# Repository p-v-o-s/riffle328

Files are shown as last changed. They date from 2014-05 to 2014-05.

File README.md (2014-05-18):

riffle328
=========

"Riffle in a Bottle"

A lower-functionality / higher cost / Arduino IDE - compatible [Riffle](http://publiclab.org/wiki/riffle), based on Atmel328p.

- Requires FTDI cable for programming (e.g. Adafruit's "FTDI Friend") -- typically $15
- Includes uSD, flash memory, high-precision real time clock (DS3231) with coin battery backup
- Programmable as "Arduino UNO" in Arduino IDE
- runs at 3.3V and 16 MHz
- includes circuit for monitoring battery level
- board width allows device to be inserted through mouth of standard plastic water bottle (one with 20 mm diameter or greater)
- can run for several weeks (perhaps months) on 3 AA batteries, especially if low self-discharging batteries (like rechargeable Eneloops) are used
- Rough estimate of cost of parts that could be used to log temperature in a water bottle (not including shipping, or FTDI cable): $38 -- cost estimate [here](https://docs.google.com/spreadsheets/d/1v0O8HmP8-q_kPunHILv5Io3zThpqvPBZZoY3aYnxRDc/edit#gid=0)

### Usage

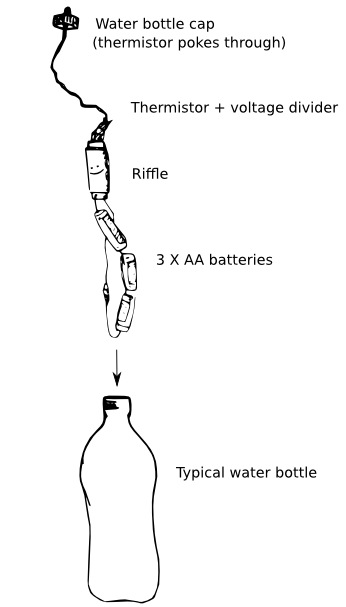
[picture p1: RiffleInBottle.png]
Optional title


- For a diagram of pin locations and optional configurations, please see this [diagram in PDF format](https://github.com/p-v-o-s/riffle328/blob/master/riffleUsage.pdf)

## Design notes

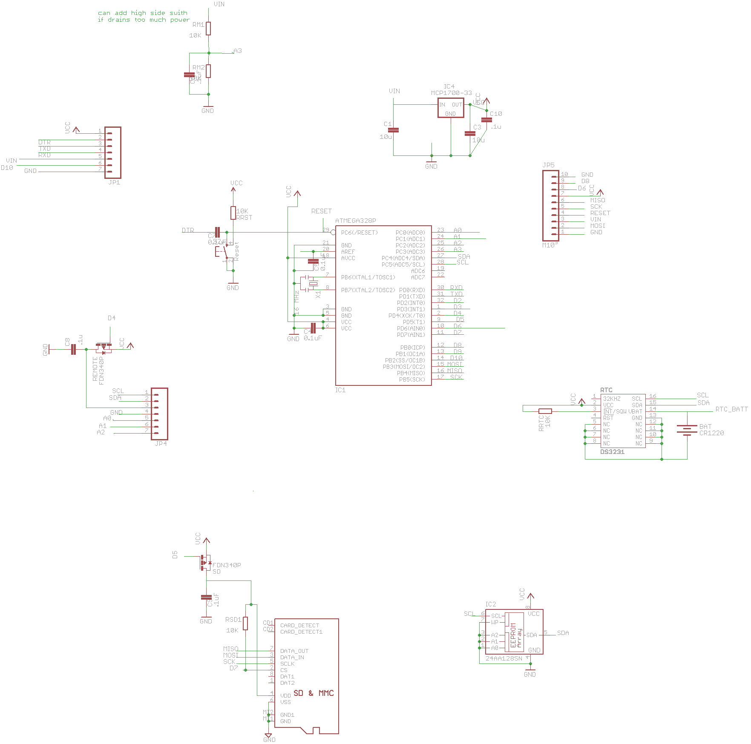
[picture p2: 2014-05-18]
REVA1/riffle328-REVA-schem.png

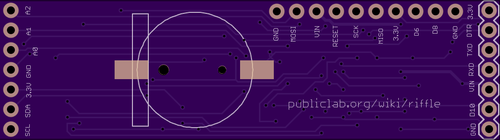
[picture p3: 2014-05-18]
REVA1/riffle328REVA-oshback.png

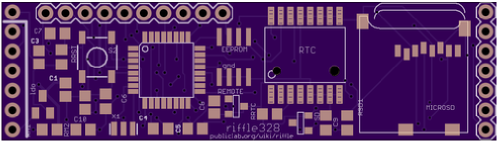
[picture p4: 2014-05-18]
REVA1/riffle328REVA-oshfront.png

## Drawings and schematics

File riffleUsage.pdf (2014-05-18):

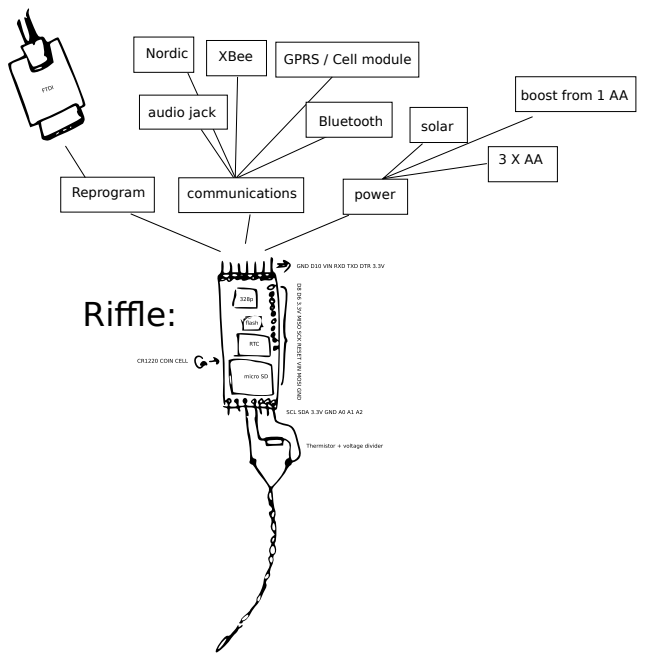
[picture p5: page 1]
Bluetooth; Riffle:; XBee; GPRS / Cell module; power; solar; Reprogram; Nordic; communications; audio jack

boost from 1 AA

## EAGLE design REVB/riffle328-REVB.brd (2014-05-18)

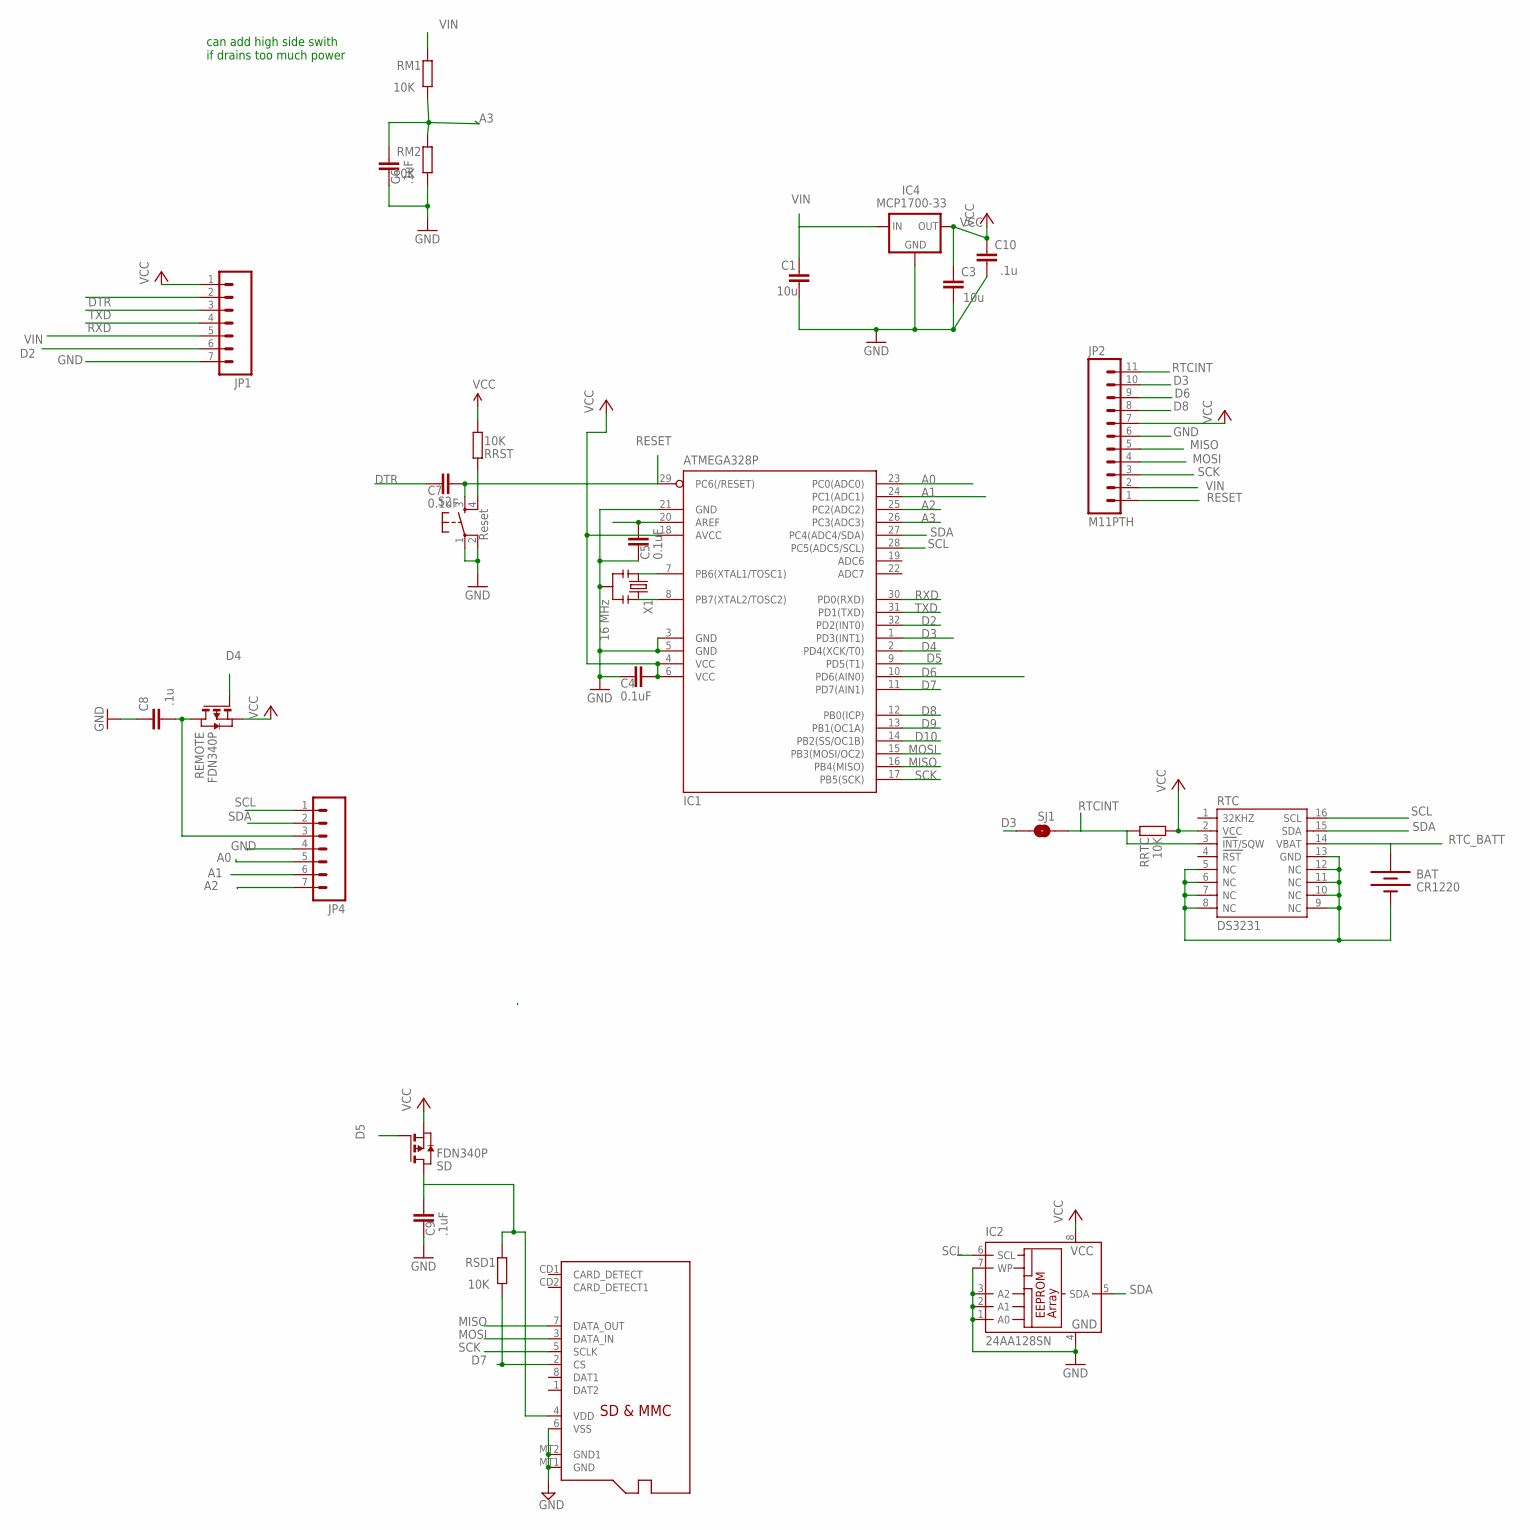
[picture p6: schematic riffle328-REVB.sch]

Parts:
BAT: CR1220; BATTCON_12MM_SMT
C1, C3: 10u; C0805
C4, C5, C7: 0.1uF; C0805@1
C6, C9: .1uF; C0805@1
C8, C10: .1u; C0805
IC1: ATMEGA328P; TQFP32-08
IC2: 24AA128SN; SO-08
IC4: MCP1700-33; SOT23
JP1, JP4: M07; 1X07
JP2: M11PTH; 1X11
MICROSD: MICROSD
REMOTE: FDN340P; SOT-23
RM1, RM2: 10K; R0805
RRST: 10K; R0805
RRTC: 10K; R0805
RSD1: 10K; R0805
RTC: DS3231
S2: Reset; TACTILE_SWITCH_SMD
SD: FDN340P; SOT-23
SJ1: SOLDERJUMPERNO; SJ_2S-NO
X1: 16 MHz; RESONATOR-SMD

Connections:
A0: IC1.23 (PC0(ADC0)), JP4.5
A1: IC1.24 (PC1(ADC1)), JP4.6
A2: IC1.25 (PC2(ADC2)), JP4.7
A3: C6.2, IC1.26 (PC3(ADC3)), RM1.1, RM2.2
AREF: C5.2, IC1.20 (AREF)
D2: IC1.32 (PD2(INT0)), JP1.6
D3: IC1.1 (PD3(INT1)), JP2.10, SJ1.2
D4: IC1.2 (PD4(XCK/T0)), REMOTE.3 (G)
D5: IC1.9 (PD5(T1)), SD.3 (G)
D6: IC1.10 (PD6(AIN0)), JP2.9
D7: IC1.11 (PD7(AIN1)), MICROSD.2 (CS), RSD1.1
D8: IC1.12 (PB0(ICP)), JP2.8
D9: IC1.13 (PB1(OC1A))
D10: IC1.14 (PB2(SS/OC1B))
DTR: C7.1, JP1.2
GND: BAT.P$1 (-), C1.2, C3.2, C4.1, C5.1, C6.1, C8.1, C9.1, C10.2, IC1.3 (GND), IC1.5 (GND), IC1.21 (GND), IC2.1 (A0), IC2.2 (A1), IC2.3 (A2), IC2.4 (GND), IC2.7 (WP), IC4.1 (GND), JP1.7, JP2.6, JP4.4, MICROSD.6 (VSS), MICROSD.MT1 (GND), MICROSD.MT2 (GND1), RM2.1, RTC.5 (NC), RTC.6 (NC), RTC.7 (NC), RTC.8 (NC), RTC.9 (NC), RTC.10 (NC), RTC.11 (NC), RTC.12 (NC), RTC.13 (GND), S2.1, S2.2, X1.2
MISO: IC1.16 (PB4(MISO)), JP2.5, MICROSD.7 (DATA_OUT)
MOSI: IC1.15 (PB3(MOSI/OC2)), JP2.4, MICROSD.3 (DATA_IN)
unnamed: IC1.8 (PB7(XTAL2/TOSC2)), X1.3
unnamed: IC1.7 (PB6(XTAL1/TOSC1)), X1.1
RESET: C7.2, IC1.29 (PC6(/RESET)), JP2.1, RRST.2, S2.3, S2.4
RTCINT: JP2.11, RRTC.2, RTC.3 (INT/SQW), SJ1.1
RTC_BATT: BAT.P$2 (+), RTC.14 (VBAT)
RXD: IC1.30 (PD0(RXD)), JP1.4
SCK: IC1.17 (PB5(SCK)), JP2.3, MICROSD.5 (SCLK)
SCL: IC1.28 (PC5(ADC5/SCL)), IC2.6 (SCL), JP4.1, RTC.16 (SCL)
SDA: IC1.27 (PC4(ADC4/SDA)), IC2.5 (SDA), JP4.2, RTC.15 (SDA)
TXD: IC1.31 (PD1(TXD)), JP1.3
VCC: C3.1, C4.2, C8.2, C10.1, IC1.4 (VCC), IC1.6 (VCC), IC1.18 (AVCC), IC2.8 (VCC), IC4.2 (OUT), JP1.1, JP2.7, JP4.3, REMOTE.1 (D), REMOTE.2 (S), RRST.1, RRTC.1, RTC.2 (VCC), SD.2 (S)
VDD: C9.2, MICROSD.4 (VDD), RSD1.2, SD.1 (D)
VIN: C1.1, IC4.3 (IN), JP1.5, JP2.2, RM1.2

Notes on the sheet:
can add high side swith if drains too much power

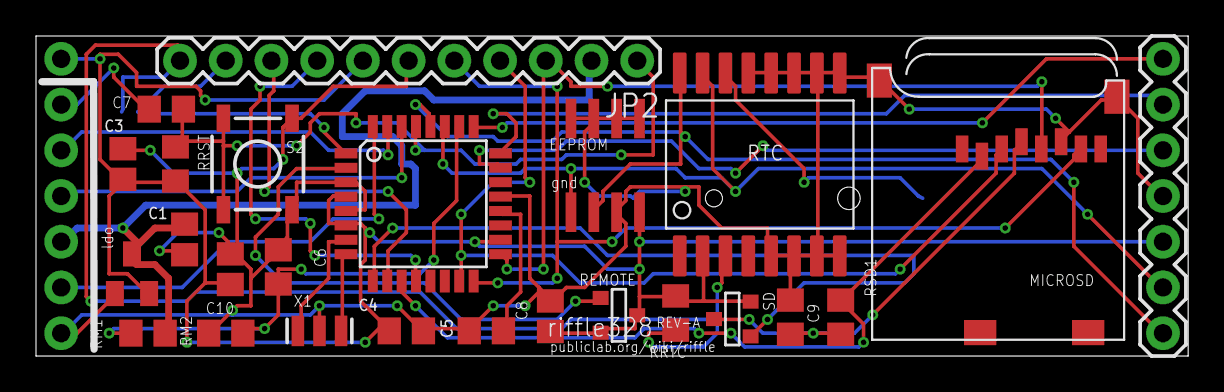
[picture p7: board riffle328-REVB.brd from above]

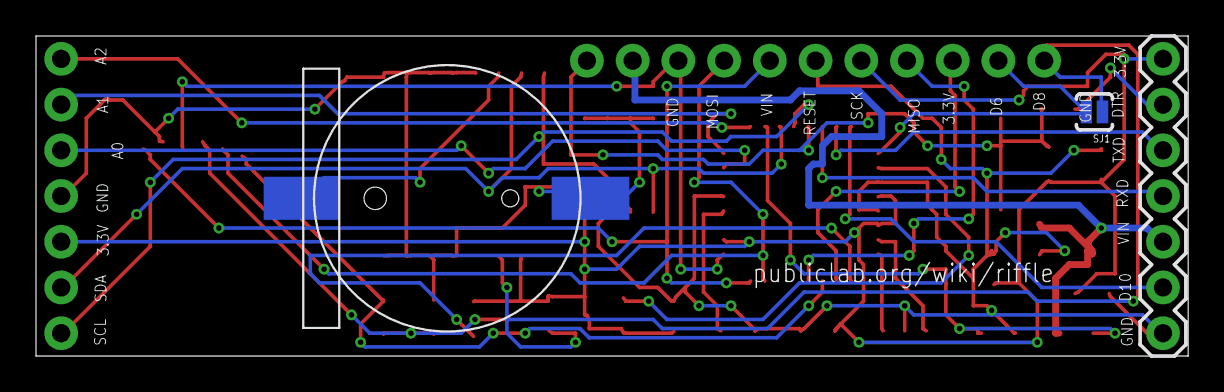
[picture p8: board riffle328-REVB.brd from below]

Board: 4 copper layers, 64.0 x 17.8 mm, 28 parts (3 on the bottom side), 29 nets.

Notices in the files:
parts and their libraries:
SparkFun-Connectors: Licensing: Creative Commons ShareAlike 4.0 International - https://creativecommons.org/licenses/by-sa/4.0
